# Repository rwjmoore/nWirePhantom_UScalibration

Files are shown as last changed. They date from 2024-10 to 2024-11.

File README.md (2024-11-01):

# nWirePhantom_UScalibration
Procedure and code for using an N-wire phantom and the [fCal](http://perk-software.cs.queensu.ca/plus/doc/nightly/user/ApplicationfCal.html) software to resolve the transformation between the ultrasound image and a marker coordinate system

# Instructions for Use

NWirePhantomTemplate contains the following information: 
- BkSettings: Necessary configuration files for the BK3500 US machine
- NdiToolDefinitions: A repository of commonly used marker files. For the intraoperative TORS study, the HoloTORSUS_V2.rom is used.
- fCal_X.X.stl: indicates the STL file used for visualization purposes in the fCal software. fCAL 2.1 is currently used, which is the 3D printed phantom
- PlusDeviceSet_fCal_14L3_NWirePhantomCalibration.xml: the xml configuration file used for fCal
- Probe and Stylus .STL files: Depending on the probe used, can select the appropriate model. The L14-5_38 is used for visualization purposes in this applicaiton

# Modifying the XML configuration file
This is the most important step in the calibration process. The key fields requiring modification are the ClipRectangleOrigin and the ClipRectangleSize, which indicate how the US frame is cropped. Your desired cropping will change depending on the US image settings (sector and depth), so be mindful about what the settings you want to calibrate to during the registration. 

# Performing the Registration 
1. Load the xml file into the fCal application and select "connect". If not connecting, make sure you computer's IPv4 settings are set to 10.0.0.4, the correct COM port for the NDI tracker is in the xml file, and you have the correct IP address of the US machine.
2. Check the capturing tab to make sure that the US image looks good. Specifically, check that the cropping produces the portion of image you want to do your analysis on.
3. The stylus calibration functionality does not work. Instead, use the stylus calibration function of the NDI tracker software if this has not been updated in a while. Once the stylus is calibrated, replace this transform in "StylusTip" To="Stylus" field in the xml file.
4. Perform the phantom calibration. This step is used to register the phantom tracker to the phantom coordinate system. If the phantom has not moved, this most likely has not changed. Regardless, you can perform this by ensuring the phantom marker is in view of the NDI tracker. Touch the different fiducials on the phantom using the stylus by following the directions in fCal to perform the registration.
5. Save the phantom calibration (if newly performed). For some reason the fCal software will crash if you redo the spatial calibration. Therefore, save the phantom calibration just in-case you need to redo the spatial calibration in the next step.
6. Submerge the phantom in a waterbath and position such that the phantom marker is in view of the NDI tracker.
7. Click on the "Start" in the Spatial Calibration tab. Move the transducer *very slowlyy* with the marker visible to the NDI tracker and the imaging plane coplanar to the face of the phantom that is longest. See notes on Troubleshooting if having trouble. You should probe a registration with submillimetre reprojection error. 
8. Save the file. Extract transform <Transform From="Image" To="Probe"> as the calibration transform.

# Troubleshooting
- If you are not finding any fiducial candidates during the spatial calibration then you most likely have changed the cropping parameters and the approximate ApproximateSpacingMmPerPixel field in the xml file is no longer accurate. Find the length of the transducer from its datasheet and divide this by the number of pixels (pixel width of your US image) and put this value into the ApproximateSpacingMmPerPixel field in the xml file.
- If you want to change the cropping, make sure to change the ClipRectangelOrigin and the ClipRectangleSize in both the <Segmentation> and the <DataSource> fields for the US.

# Additional Tools
- The two files " NWirePhantomCalibration_5cm120sector " and " NWirePhantomCalibration_4cm120sector " are already cropped to the described depth and sector with the 14L3 probe. Note that these also have phantom calibrations and a spatial calibration present in these files, which is useful for seeing what they look like.
- MATLAB script "processTransform.m" is useful for assessing performance of registration. It will tell you the reprojected width and depth of the US image, which you can compare with transducer width and imaging depth 
- For coordinate systems and description of the fCal software: http://perk-software.cs.queensu.ca/plus/doc/nightly/user/ApplicationfCal.html
- Method used to register the image to the probe tracker coordinate system: https://doi.org/10.1007/s11548-013-0904-9

PLUS CAD files: http://perk-software.cs.queensu.ca/plus/doc/nightly/modelcatalog/

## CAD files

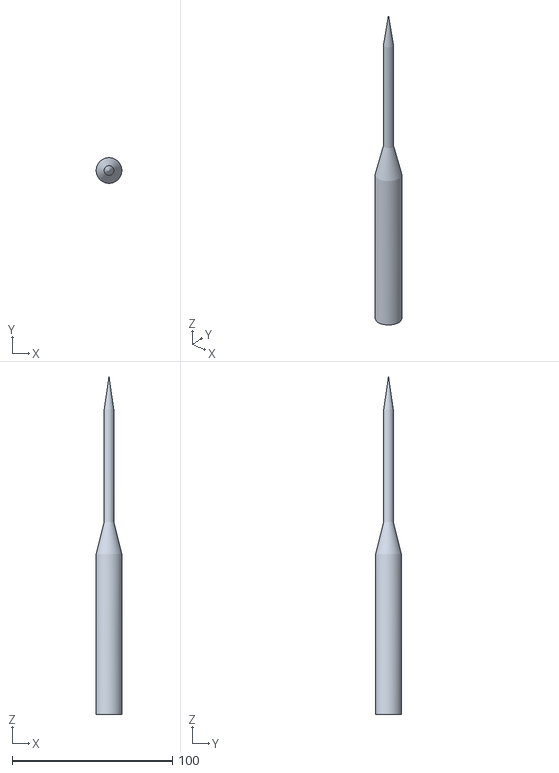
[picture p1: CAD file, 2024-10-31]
NWirePhantomTemplate/Stylus_Example.stl
16.0 x 16.0 x 210.0

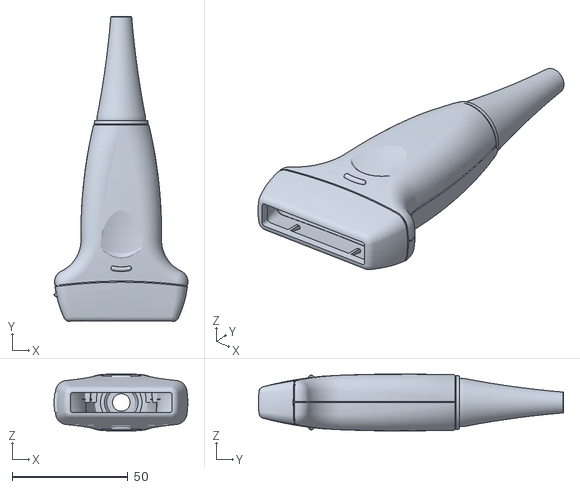
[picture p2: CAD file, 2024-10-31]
NWirePhantomTemplate/Probe_L14-5_38.stl
57.9 x 132.0 x 24.6

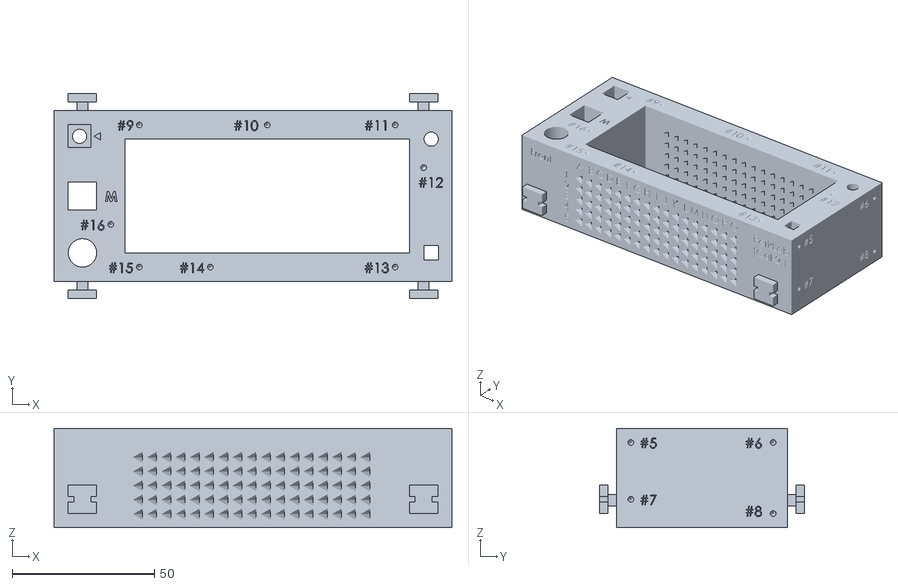
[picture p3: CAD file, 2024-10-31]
NWirePhantomTemplate/fCal_2.1.STL
140.0 x 72.0 x 35.0

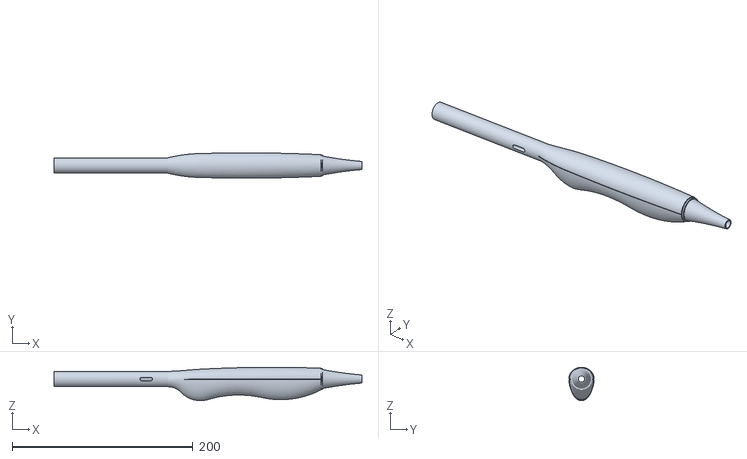
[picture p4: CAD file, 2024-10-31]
NWirePhantomTemplate/Probe_EC9-5_10.stl
341.0 x 28.0 x 37.0
